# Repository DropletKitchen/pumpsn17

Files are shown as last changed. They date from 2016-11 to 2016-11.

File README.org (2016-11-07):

* Low-cost, High-performance Syringe Pumps for Microfluidics Applications

*This page describes how to build simple but high quality syringe pumps for microfluidics applications.*

This is a [[https://DropletKitchen.github.io][DropletKitchen]] project. Original source code of the project
is provided under MIT License. The source may contain code under a
different license, if this is the case it is stated in the LICENSE
file.

If not stated otherwise, the designs and documentation in this repository
is Copyright (c) 2016 Martin Fischlechner and DropletKitchen Contributors,
and made available under a
[[https://creativecommons.org/licenses/by/4.0/][Creative Commons Attribution 4.0 International (CC BY 4.0)]] License.

#+CAPTION: Image of the 3D-printed version of the pump.
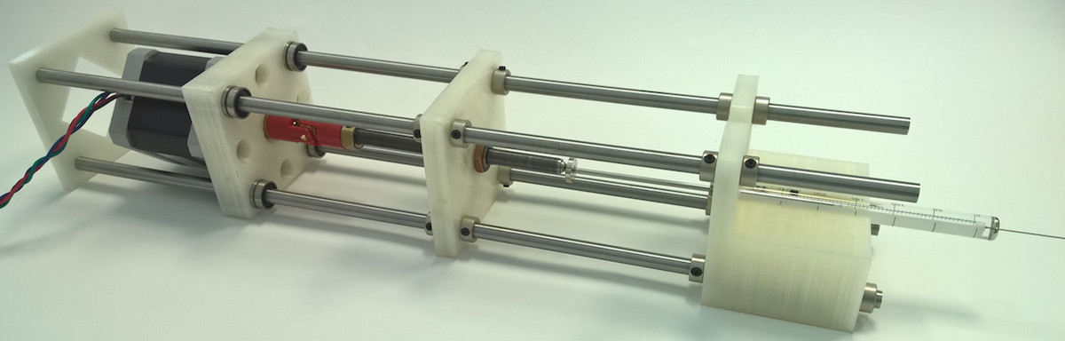
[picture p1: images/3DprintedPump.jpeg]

#+BEGIN_QUOTE
Image of the 3D-printed version of the pump.
#+END_QUOTE

** Introduction

These syringe pumps are infusion (push) only and have been designed to
be as simple as possible. We are using them for droplet microfluidics
and other microfluidics applications. They rival the performance of
commercial-grade, high-quality pumps and are suitable for professional
research.

To achieve constant flowrates without depending on an overly sturdy
structure, the leadscrew itself actuates the movement of the syringe
piston. This way, the pump only has to be rigid and aligned between
the parts holding the nut of the leadscrew and the syringe. Different
syringe diameters can be used by applying simple 3D-printed adaptors.
Screws and nuts for optics assemblies are employed, which, in
conjunction with microstepping the motor, result in stable flow even
at very low flowrates. The pump uses it's structural components as
endstops, and the user controls the system via a software frontend
based on Pure Data (Pd), a graphical programming language, which
allows for straightforward and live system automation, at a small
fraction of the cost of a commercial pump.

** Mechanics - Files and Bill of Materials   

*** Pump Design files (openSCAD)

To be able to adapt the design towards other hardware, we modelled it
in openSCAD (http://www.openscad.org/) in parametric form. Using the
Bill of Materials, BOM, below it should work out-of-the box, else you
will have to adapt the model. Please check dimensions first before
laser cutting/3D printing parts. In openSCAD, the variables are
defined in the header of the file, the rest of the code generating the
model then works with those values. This means it is very
straightforward to adapt the design towards your specific
requirements. In our experience, measuring sizes with a caliper and
directly putting these values into the model yields tight-fitting
parts once laser-cut. With a Fused Deposition Modelling, FDM,
3D-printer you should make some test prints first ('fit' depends on
material characteristics, print settings and the calibration of your
machine). Although you can make parts fit by filing and drilling, this
is cumbersome and should be avoided.

#+CAPTION: A screenshot of the pump in openSCAD (for the file see [[./files/SyringePump3Dmodel.scad]]).
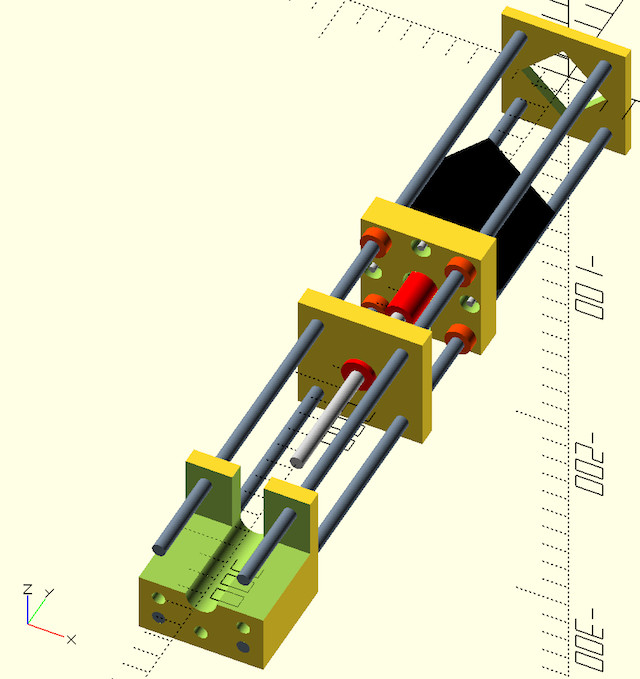
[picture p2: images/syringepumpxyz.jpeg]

#+BEGIN_QUOTE
A screenshot of the pump in openSCAD (for the file see
[[./files/SyringePump3Dmodel.scad]]).
#+END_QUOTE

#+CAPTION: Simple 3D-printed syringe adaptors to allow the use of syringes with different diameters (see [[./files/3DprintedSyringeAdaptors.scad]]). 
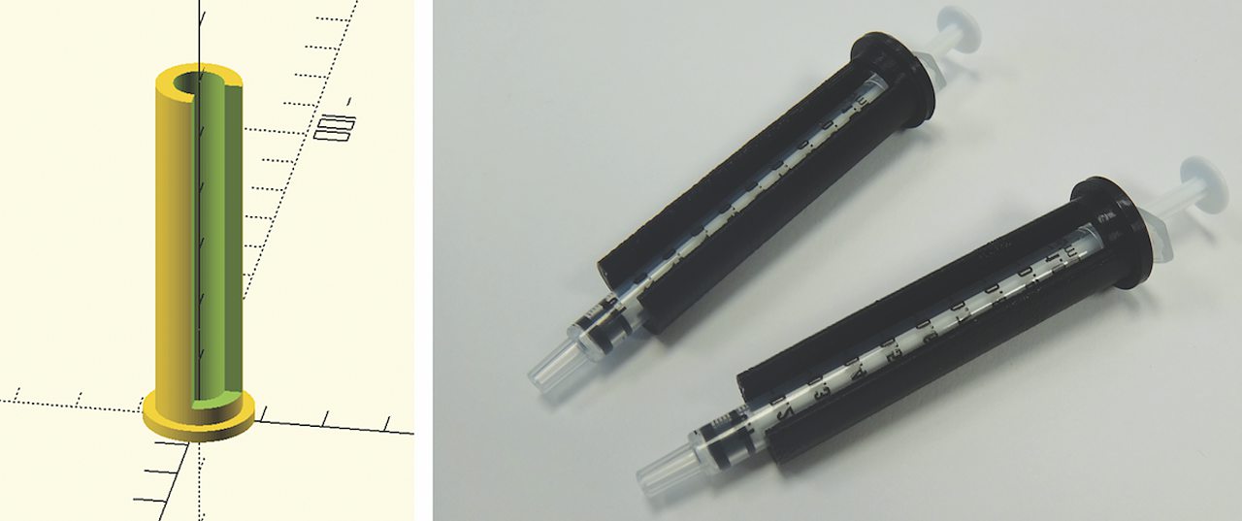
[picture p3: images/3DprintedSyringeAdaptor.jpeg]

#+BEGIN_QUOTE
Simple 3D-printed syringe adaptors to allow the use of syringes with
different diameters (see [[./files/3DprintedSyringeAdaptors.scad]]).
#+END_QUOTE

*** Bill of Materials

- this list is for a set of 4 syringe pumps, which should be
  sufficient to drive most microfluidic protocols. Cost of components
  is approximate.

| item [4X Syringe Pumps]                                        |      number | purpose               | bought from   |  part-no | approx  (£/euro) |
|----------------------------------------------------------------+-------------+-----------------------+---------------+----------+-------------|
| Allegro A4983 Based Stepper Boards: here the 'Big Easy Driver' |           4 | stepper board         | Technobots    | 2900-445 | ~ 70        |
| Nema 17 Steppers (400 steps/rev)                               |           4 | stepper motor         | Technobots    | 1402-050 | ~ 80        |
| Teensy 3.1 or 3.2 Microcontroller                              |           1 | control               | cpc-Farnell   |  SC13539 | ~ 20        |
| Fine Hex Adjuster, 1/4"-80, 4" Long                            |           4 | leadscrew             | Thorlabs      | F25SS400 | ~ 40        |
| Locking Phosphor-Bronze Bushing with Nut, 1/4"-80, L=0.50"     |           4 | leadscrewnut          | Thorlabs      |   N80L6P | ~ 28        |
| Silver Steel 6mm x 333mm                                       |          16 | pump structure        | Technobots    | 4426-006 | ~ 35        |
| Zinc Collets 6mm pk/4                                          |          24 | fasteners             | Technobots    | 4609-060 | ~ 28        |
| Linear Bearing LM6UU 6mm Bushing                               |          16 | slides motorpart      | Technobots    | 4604-606 | ~ 16        |
| Universal Coupling Body                                        |           4 | motor-screw-connector | Technobots    | 4604-050 | ~ 12        |
| Universal Coupling Insert - 5mm                                |           4 | motor-side            | Technobots    | 4604-059 | ~ 8         |
| Universal Coupling Insert - 1/4"                               |           4 | screw-side            | Technobots    | 4604-066 | ~ 8         |
| OTHER SMALL ITEMS                                              |             |                       |               |          |             |
| 95mm x 127mm Copper Clad Stripboard (or bigger)                |           1 | mount for electronics | Technobots    |          | ~ 2         |
| Male & Female PCB Headers 2.45mm pitch                         |        some | simple connectors     | cpc-Farnell   |          | ~ 10        |
| Sugru (good to isolate PCB-header-based connectors)            |             | or use hotglue-gun    | Maplins       |          | ~ 7         |
| Screws M3 (25mm): to mount motors                              |          16 |                       | Technobots    | 4300-006 | ~ 3 for 100 |
| Screws M3 (<10mm), optional                                    |        many | fix collets better    | Technobots    | 4300-002 | ~ 2 for 100 |
| Screws M6 (~100mm), syringe part lasercut version              |           8 | reduces acrylic       | hardware shop |          |             |
| USB (micro) cable                                              |           1 |                       | cpc-Farnell   |          | ~ 3         |
| 6 wire colored ribbon cable                                    |          4m |                       | Technobots    |          | ~ 3         |
| 12V/>=5A power supply                                          |           1 |                       | cpc-farnell   |          | ~ 20        |
| 3D-printer filament (PLA) or 5mm acrylic sheets(410X280)       | 1kg/5sheets | pump structure        | RS, Techsoft  |          | ~ 30        |
|----------------------------------------------------------------+-------------+-----------------------+---------------+----------+-------------|
|                                                                |             |                       |               | 4 pumps: | ~ 425       |

**** Companies:
- Technobots:  http://www.technobotsonline.com
- Thorlabs:    http:/www.thorlabs.com
- CPC-Farnell: http://cpc.farnell.com/
- RS:          http://uk.rs-online.com/web/
- Techsoft:    http://www.techsoft.co.uk/
- Maplin:      http://www.maplin.co.uk

All components but the optics-screws (Thorlabs) can be obtained
commercially. If other leadscrews are used, the software has to be
adapted to the distance/revolution grading.

**** Machines (and/or):
- Lasercutter (we used an Epilog, 30W): Often found in a local
  hackerspace or University Engineering Department. One could also use
  internet-based services.
- FDM 3D-printer (we use an Ultimaker 2 & PLA (natural white) material)

**** Tools:
- Soldering iron
- Hand tools (screwdrivers etc.)

** Mechanical Assembly of Pumps
*** Laser-cut version
- adapt the openSCAD model to your needs by changing the variables as
  you see fit and rendering the model.

- export .stl-files of all the parts (syringe-part, leadscrew-part,
  motor-part, end-part). It is easiest to comment-out all parts but
  one, render and export to .stl.

- import the .stl files into openSCAD, orient them so that the
  projection you want is at (0,0,0). Render and export as .dxf-file,
  which can then be directly used by a laser cutter.

  #+BEGIN_SRC C :exports code      
  projection(cut=true) 
  translate ([0, 0, 0]) 
  rotate ([0,0,0])
  import("/pathtofile/file.stl"); 
  // comment projection out first, adjust translate/rotate (slices at 0,0,0),
  // uncomment projection(cut=true),render, export to .dxf
  #+END_SRC

- cut out all the parts. It might be a good idea to check dimensions
  and fit first by cutting a trial sample.

- if you use the components from above, you should be able to use the
  .dxf-file provided ([[./files/PumpPartsLaserCut.dxf]]; see
  below). To work with 2D-CAD files we use the free version of
  Draftsight
  (http://www.3ds.com/products-services/draftsight-cad-software/free-download/).

#+CAPTION: Left: Laser cut parts for one pump. Right: Image of components.
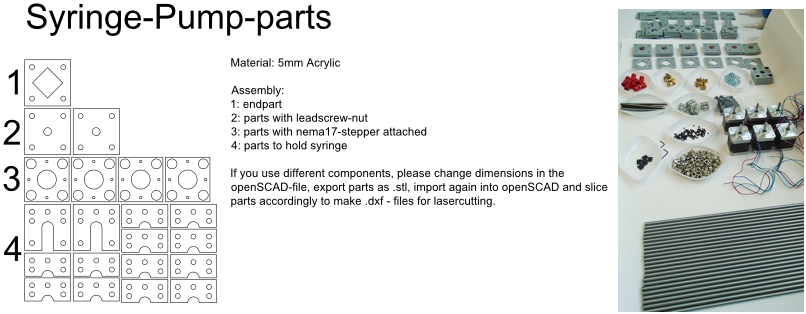
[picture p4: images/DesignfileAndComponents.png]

#+BEGIN_QUOTE
Left: Laser cut parts for one pump. Right: Image of components.
#+END_QUOTE

**** Pre-Assembly of Parts
***** Motor Part
- tin the leads of the motors with solder, add a male
  PCB-connector (or any other connector of your choosing. On our
  motors the colored leads are GREEN, BLACK, BLUE, RED).
- we use Sugru to electrically isolate the connectors at the end.
- add the connector for the leadscrew (5mm brass insert) to the
  motor - you might not have space to do that later.
- depending which length of M3 screws you have used to mount the motor, you
  will need different quantities of acrylic sheets. LM6UU bearings are
  19mm in length, so 4X5mm sheets are fine. If you have longer screws,
  either add nuts or fit in some more acrylic sheets.
- slot the 4 bearings into the stack of parts (should be lightly
  press-fit); screw the assembly together. The bearings do not have to
  bear much load. If they aren't fixed well enough use a dab of epoxy glue.

***** Leadscrew Part
- take the two acrylic sheets and mount the leadscrew-nut.
- add the brass insert to connect the motor onto the leadscrew
- insert the screw VERY carefully to avoid damaging the thread which can
  happen rather easily.

#+CAPTION: Pre-assemble motor with leadscrew (bottom right) and component inventory.
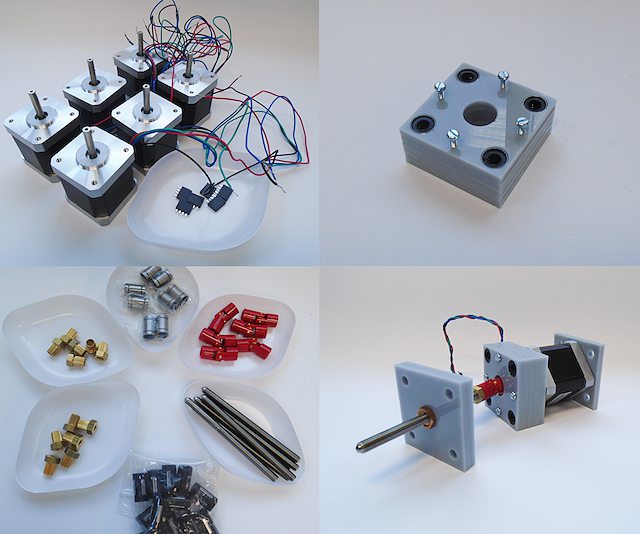
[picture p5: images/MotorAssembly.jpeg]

#+BEGIN_QUOTE
Pre-assemble motor with leadscrew (bottom right) and component inventory.
#+END_QUOTE

***** Syringe Part
For this part one should design towards specific needs. 
Make sure the cutouts are big enough for your syringes. If you want to
use different syringes with different diameters, adjust the
CAD-model to the thickest diameter and 3D-print/laser cut adaptors that
can be quickly exchanged.The adaptors must allow the piston of
the syringe to reside exactly in the centerline of the screw.

You can either cut many slides and assemble as a stack, or use some
long M6 screws and attach pairs of parts with M6 nuts. If you use tape
to hold the syringes in place (which works fine), filling the
structure with acrylic plates provides a continuous surface for fixing
the tape in place.

**** Assembly of the Pump
- take 4 of the 6mm steel shafts, round off the edges with a file to
  ease assembly.

- slot the steel shafts into the assembled motor part. Take care not
  to harm the LM6UU linear bearings. 

- add endpart, leadscrew-part and syringe part. Do not forget to
  insert the collets (8 collets/part, before and after). Don't fix
  them yet.

- measure the length of the syringes you want to use. There is no
  electronic endstops put into the design to keep assembly-time to a
  minimum (although it could be done rather easily). To make sure that
  your (glass) syringes stay unharmed, the length between the syringe-
  and the leadscrew part should be adjusted such that the movement
  will be blocked mechanically before crushing the syringe. The
  endpart should be mounted such that the movement will be blocked
  before the leadscrew turns itself out of its nut. If the motor hits
  these points it will stall, making a different noise than usual, but
  else stay unharmed. Don't forget to adjust the power of the motor on
  the respective potentiometer on the stepper driver board. With
  maximal power applied, the stepper motor can damage the assembly.

#+CAPTION: Three pumps before adjusting the leadscrew part & fixing everything with collets.
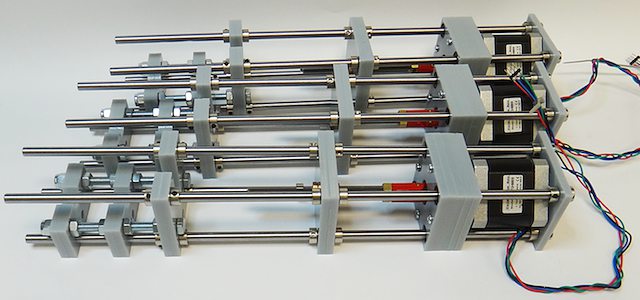
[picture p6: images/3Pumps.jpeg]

#+BEGIN_QUOTE
Three pumps before adjusting the leadscrew part & fixing everything
with collets.
#+END_QUOTE

- fix the collets of the syringe part. In general it is a good idea to
  use short M3-screws instead of the small hex-screws provided for
  making repeated opening/closing easier.

- add the electronics to the motor and drive it back and forth (at
  this point you could add some lithium grease or other lubricant).
  The leadscrew-part has to be adjusted such that the turning
  leadscrew stays centered without wobble. Use your syringes to adjust
  the length between leadscrew and syringe part. This serves as a
  mechanical endstop for forward movement. Handle the position of the
  endpart accordingly to stop backward motion. Then fix the collets
  securely.

- when finished use a bit of epoxy glue to permanently connect the
  'universal coupling body' with the brass inserts. The assembly can
  still be taken apart by loosening the grub-screws holding the motor
  shaft and the leadscrew together.
 
- done!     

*** 3D-Printed Version
Depending on the calibration of your FDM-printer, parts might need
some 'adjustments'. Please print calibration pieces first to make sure
the parts are well fitting. If needed, you can use a drill-bit or a
round file to make adjustments but it is not much fun. Assembly of
pumps is similar to the lasercut version. To generate the .stl-files
for printing, it is easiest to comment out all parts but one in the
openSCAD model, render and export.

#+CAPTION: Two modified 3D-printed pumps with smaller, lower power Nema14 motors used in a microfluidic experiment. The electronics in the image is based on a 'Quadstepper board' (unfortunately no longer available). 
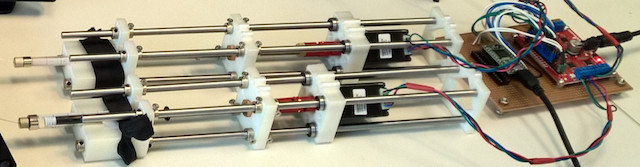
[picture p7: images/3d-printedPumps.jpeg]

#+BEGIN_QUOTE
Two modified 3D-printed pumps with smaller, lower power Nema14 motors
used in a microfluidic experiment. The electronics in the image is
based on a 'Quadstepper board' (unfortunately no longer available).
#+END_QUOTE

** Electronics
To drive the stepper motors of the pumps we use a A4983 stepper driver
chip from Allegro Microsystems (datasheet
http://www.technobotsonline.com/Datasheets2/1518-009-A4983SETTR-T.pdf).
For convenience we use one 'Big Easy Driver' for each motor
(http://www.technobotsonline.com/big-easy-driver.html,
http://www.schmalzhaus.com/BigEasyDriver/). The 'Big Easy Driver'
boards are nice, because they default to 16 step microstepping mode,
when the 'MS1, MS2, MS3' pins are left unconnected (which means that
less soldering has to be done). With 16-step microstepping, one
revelation of the leadscrew (318 micrometer movement) is divided into
400*16=6400 steps resulting in a stable flow even at very low
flowrates. If you use a stepper with 200 steps/revolution (1.8 instead
of 0.9 degrees/step), the pumps will still work very well but you will
have to adjust the calibration in the software. If you are prepared
for some more soldering, any stepper driver board used in common FDM
3D-printers should do just fine. The stepper drivers are controlled
with a teensy 3.1 or 3.2 microcontroller. The teensy has 3.3V logic
levels, so put a solder-blob onto the stepper drivers to switch them
from 5V (default) to 3V logic.

#+CAPTION: Left: Images of the electronics board with three stepper driver boards mounted. Right: Schematic diagram.
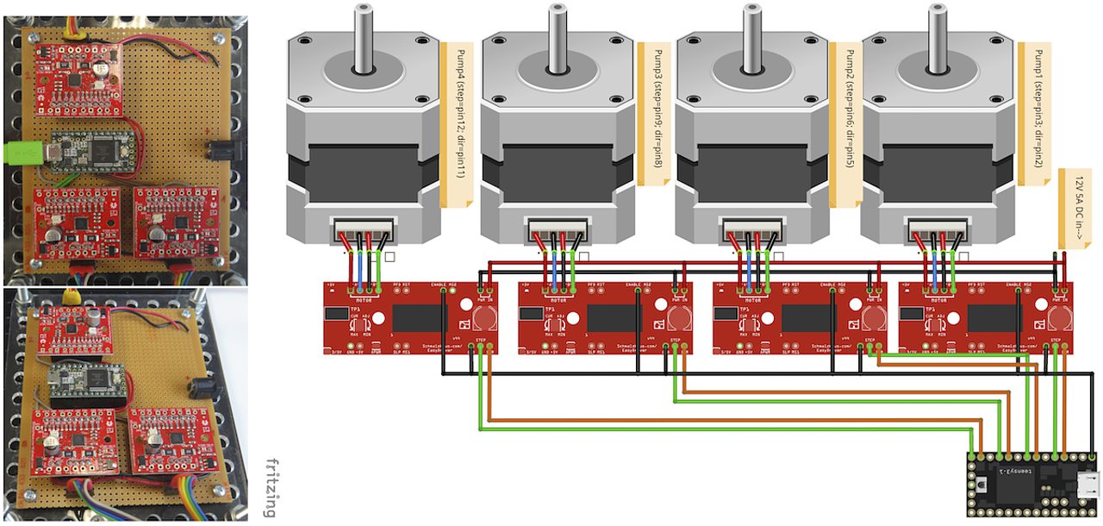
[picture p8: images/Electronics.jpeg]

#+BEGIN_QUOTE
Left: Images of the electronics board with three stepper driver boards
mounted. Right: Schematic diagram.
#+END_QUOTE

*** Make the board
- solder connectors onto the driver board (e.g. PCB-connectors)

- layout the parts on a stripboard and drill holes so that you can
  mount the board with screws to an enclosure (e.g. from laser-cut
  acrylic).

- solder female PCB-connectors on the board for the teensy and the
  stepper boards (don't forget to cut the traces on the stripboard
  underneath).
- make all the necessary connections (see layout...)

- we made the system as simple as possible: 
  - no connection to MS1, MS2, MS3 - all are pulled high when not
    connected (means the driver defaults to 16 microstep-mode
  - no connection to sleep (slp) and reset (rst) - if powered the
    system will be on all the time. If you want to shut down the
    motors, turn off the power.
 
  - this leaves only the following connections to be made:
    - enable (en) is pulled low on all by connecting to ground (this
      is important, else the pins float).
    - shared GND between teensy and the quadstepper board (or single
      big easy drivers)
    - step-pin (stp): if high for >1 microsecond, the motor will step
    - direction-pin (dir): high/low sets the direction (if your pump
      steps the 'wrong' direction, just reverse the connections of the
      leads from (e.g. green, black, blue, red --> to red, blue,
      black, green).

  - Teensy is powered by a USB connection and the motors are powered
    separately (we use a 12V 5A power supply).

- Don't forget to adjust the current supplied to the motor with the
  small potentiometer on the stepper driver board. On max, the chip
  gets hot and the motor might have enough torque to continue beyond
  the end-stop, damaging the pump assembly.

* Software for Syringe Pumps
** Introduction - mode of operation and choice of tools

The pumps are controlled with a microcontroller (a 'teensy' 3.2 or
3.1) and a software front end written in Pure Data (PD). The teensy
(https://www.pjrc.com/teensy/teensy31.html) is a 3.3V, 32-bit ARM
based microcontroller that is compatible with the Arduino toolchain
(https://www.arduino.cc/en/Guide/HomePage) and therefore easy to
program. The prime reason to use a teensy is the high speed USB data
transfer they allow
(https://www.pjrc.com/teensy/benchmark_usb_serial_receive.html). Apart
from controlling machinery, the teensy is well suited for data
acquisition tasks.

Pure Data (PD, https://puredata.info/) is an open source dataflow
programming language used primarily for music and video applications.
It runs on nearly every computing platform, is straightforward to
learn and can be modified 'live', which is great for microfluidics
experimentation.

The communication protocol between the microcontroller and PD is OSC
('Open Sound Control', https://www.opensoundcontrol.org). It is a very
flexible, easy to use two-way communication.

#+CAPTION: System diagram.

#+BEGIN_QUOTE
System diagram.
#+END_QUOTE

** Install the Software Toolchain
*** Arduino/Teensyduino
The easiest way to program teensy microcontrollers is to use the
Arduino IDE (download:https://www.arduino.cc/en/Main/Software). For
the teensy microcontrollers to be recognised by the Arduino IDE, one
must additionally install 'Teensyduino' (download:
https://www.pjrc.com/teensy/td_download.html). There is a detailed
tutorial on software installation and its use on the webpage. Most of
the Arduino libraries are compatible with teensy, Teensyduino itself
comes with many optimized ones (full install recommended).

*** Install Pure Data (PD) 
Pure Data can be downloaded from the PD community site
(https://puredata.info/downloads) and installation is straightforward.

For Mac or Win you should choose to install PD-extended, which is
pre-packaged with many additional externals from the community (all
necessary things needed for this project should be installed per
default). PD-extended is not actively maintained any more, but still
works well. Alternatively you can use PD-Vanilla and install externals
via the 'deken'-plugin (https://github.com/pure-data/deken) as
required.

On a Linux system, you should use 'PD-L2ORK'
(http://l2ork.music.vt.edu/main/make-your-own-l2ork/software/), an
up-to-date, maintained and beautified version of PD-extended from the
'Linux Laptop Orchestra' (Virginia Tech Music Department). Beta
versions for Mac and Win are now also available. PD-L2ORK runs well on
Ubuntu, but also under Raspbian on Raspberry Pi Model 2 and 3. This
allows a small touchscreen interface to be used resulting in a
small-footprint solution.

#+CAPTION: Raspberry Pi Model 3 based  to control syringe pumps. The files for the lasercut enclosure are based on a design by Sparkovsky on Thingiverse (https://www.thingiverse.com/thing:1441432).
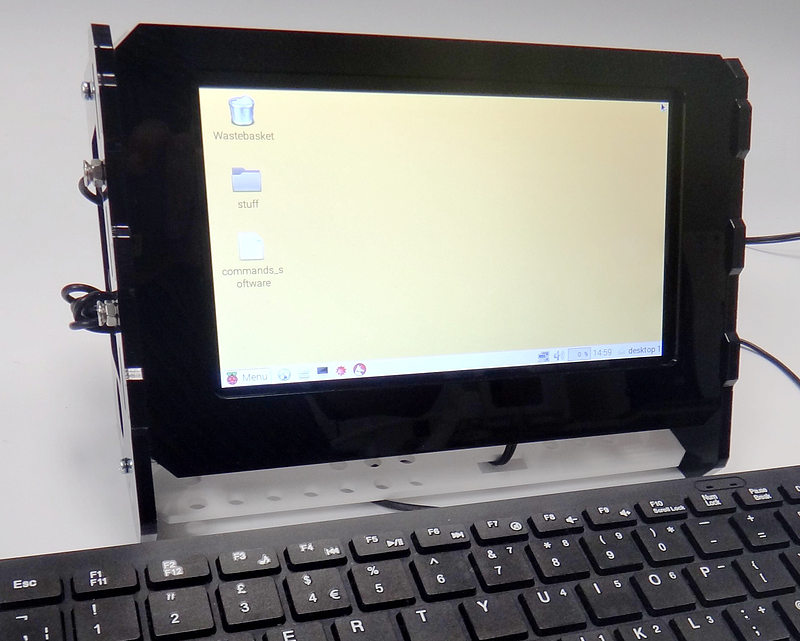
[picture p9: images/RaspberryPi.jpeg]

#+BEGIN_QUOTE
Raspberry Pi Model 3 used to control syringe pumps. The files for the
lasercut enclosure are based on a design by Sparkovsky on Thingiverse
(https://www.thingiverse.com/thing:1441432).
#+END_QUOTE

** Setting up the System 
- program the teensy
- open the PD-program 
     - and you should (almost) be ready to go. 

You can test the system without the microcontroller attached to the
pumps. If the communication works via OSC, the flow rates you transfer
(in microL/h) and the direction of movement will be mirrored in the
smaller sliders beneath the main control elements in the PD-frontend.

** How the System Works  
In a nutshell, the desired flowrate (in uL/h) is converted into a
delay time (in microseconds) which defines when the motor on the pump
has to step. To make this delay time as precise as possible, an
interrupt routine is used that checks every 10 microseconds if a motor
has to be stepped or not - no matter what the rest of the program is
doing at that time. Flow rate to delay time conversion is dependent on
the type of motor (steps/rev), thread-type of the leadscrew used
(microns/revolution) and syringe diameter.

We supply two versions of the programs here that differ where these
calculations take place:
 
- 'Hardcoded': directly on the microcontroller (PD transfers the flow
  rate value, the syringe diameter and other values are to be changed
  in the program running on the teensy). This is convenient if one
  always works with syringes of a certain diameter.
- 'Flexible': all calculations are done in PD and the resulting delay
  times in microseconds are transferred. This allows all parameters in
  PD to be changed on the fly without reprogramming the
  microcontroller when changing hardware.

** Getting it to Run
*** 'Hardcoded' Version (calculations on the teensy)
- upload the corresponding file to the microcontroller
  ([[./files/Hardcoded4Pumps.ino]]). Have a look at the code, everything
  you can and might have to change should be explained in the
  comments.
- place the PD-program ([[./files/Hardcoded4Pumps.pd]]) together with a
  little helper-program for OSC ([[./files/o.io.slipserial.pd]]) in a
  folder and open it in PD-extended or PD-L2ORK.

#+CAPTION: Screenshot of the program. 
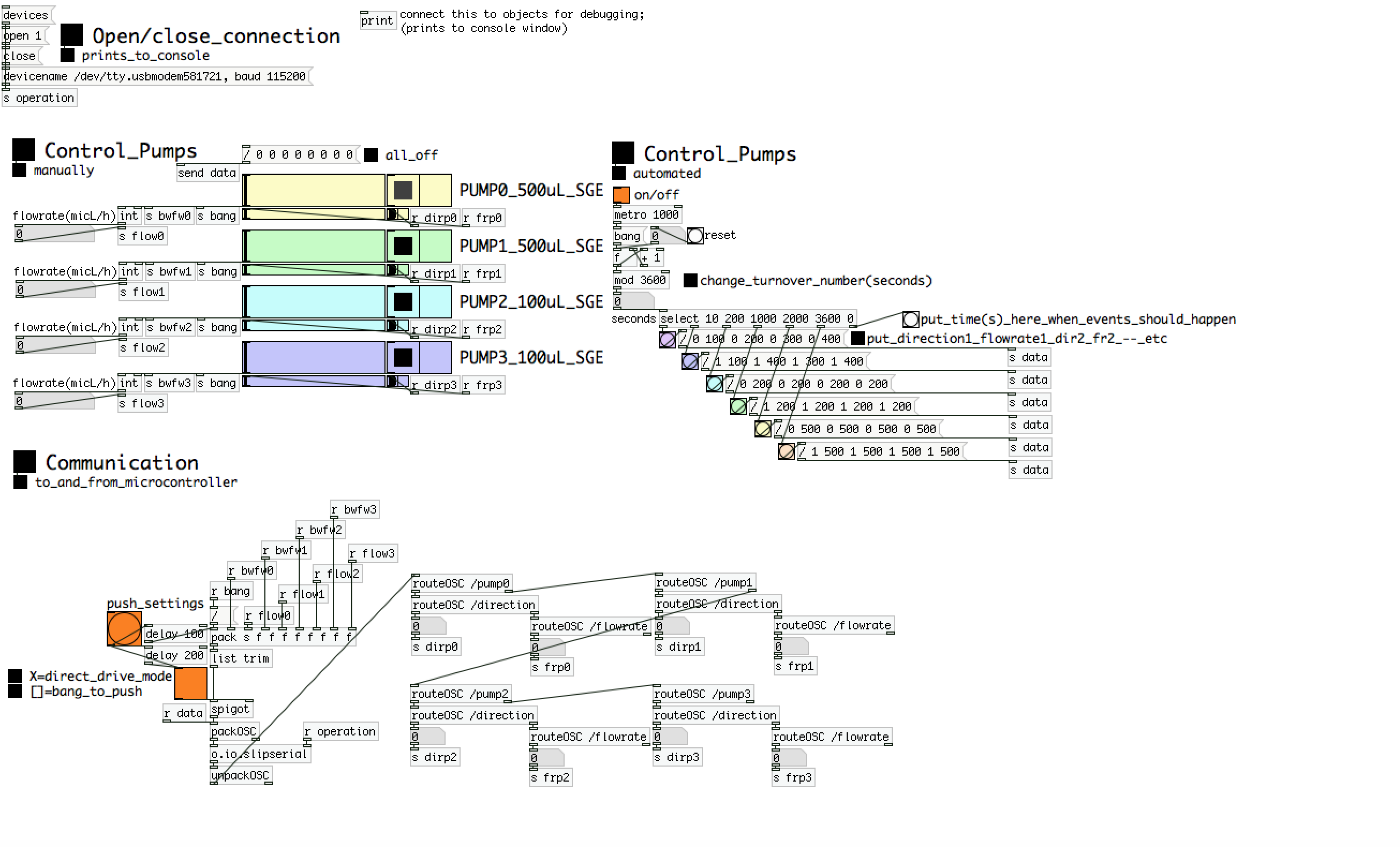
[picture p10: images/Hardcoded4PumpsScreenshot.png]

#+BEGIN_QUOTE
Screenshot of the program. 
#+END_QUOTE

- Hit [devices], and the available serial ports will show in the
  console window. One of them is connected to the teensy. Click [open
  x[ (change the numbers by entering editing mode, ctrl-e (linux),
  cmd-e (mac)) and PD should connect to the teensy.

- The section 'Control Pumps Manually' allows you to dial in your
  desired flow rate for each pump. The buttons on the right side of
  the sliders will change direction. If you right-click on an item/box
  a properties and help dialog is available which lets you learn and
  customize. If the values are transferred to the teensy, the
  microcontroller will send the list of numbers back. Those are
  displayed underneath and give immediate visual feedback. If you have
  the pumps connected and powered, you should see the changes there
  too.

- To transfer the pump settings, you have to click the orange 'bang'
  in 'Communication to and from microcontroller'. For immediate
  response when changing settings, click the orange toggle switch to
  mark it [X].

- 'Control Pumps Automated' is a simple tool for automation. Setting
  the toggle-switch to 'on' [X] activates a counter (per default here
  in seconds) which will turnover to 0 after some time (here 1h). The
  [select] box activates the attached lists of numbers (direction
  pump1 flowrate pump1 ....) after the dialled-in times. To change it,
  get into edit-mode, change the values and the numbers of events to
  your liking (you will have to copy/paste/delete structures and
  reconnect).

*** 'Flexible' Version (calculations in PD) 
This version of the programme is reduced in its footprint to be
displayed on a 7" screen (in our case a raspberry Pi Model 3 with a
touchscreen). It uses PD's 'Graph on Parent (GOP)' feature which
allows program complexity to be hidden. It is used similarly as above,
but lets you select serial ports as well as syringe diameters. The
right-hand part outside the 'GOP' can be modified for more complex
automation.

#+CAPTION: Screenshot of the program. 
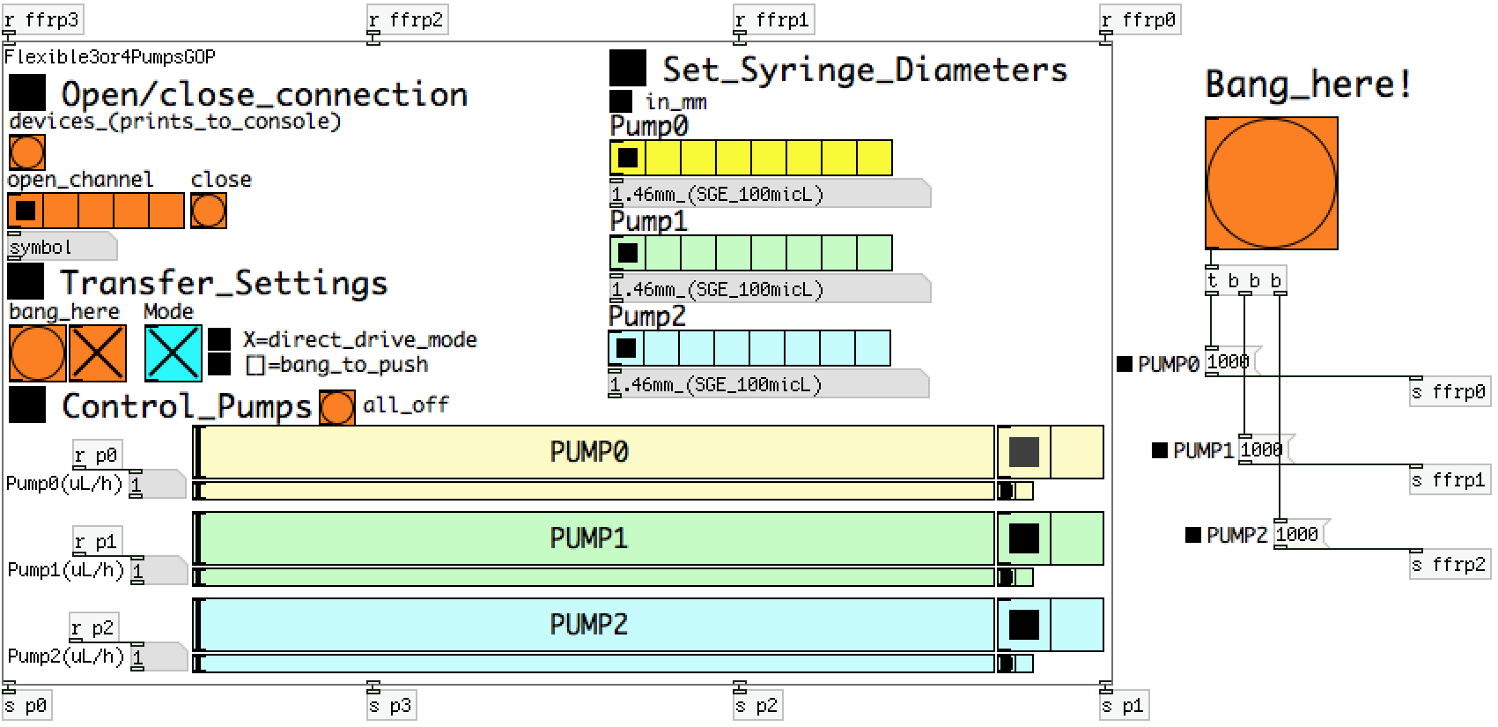
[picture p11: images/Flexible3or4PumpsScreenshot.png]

#+BEGIN_QUOTE
Screenshot of the program.
#+END_QUOTE

- upload the corresponding file to the microcontroller
  ([[./files/Flexible3or4Pumps.ino]]).
- place the PD-programs ([[./files/Flexible3or4Pumps.pd]]) and
  ([[./files/Flexible3or4PumpsGOP.pd]]) together with a little
  helper-program for OSC ([[./files/o.io.slipserial.pd]]) in a folder and
  open it in PD-extended or PD-L2ORK.
- The file 'Flexible3or4Pumps.pd' is the software front end. If you
  want to change the program in any way, changes have to be conducted
  in 'Flexible3or4PumpsGOP.pd'. The program actually contains controls
  for 4 pumps, but only 3 are shown in the front end. To have a 4-pump
  system, enlarge the red 'GOP' rectangle and move the controls for
  the 4th pump into the space. It will then show in the front end. The
  calculations in 'Flexible3or4PumpsGOP.pd' should be simple to adapt
  to modified hardware.

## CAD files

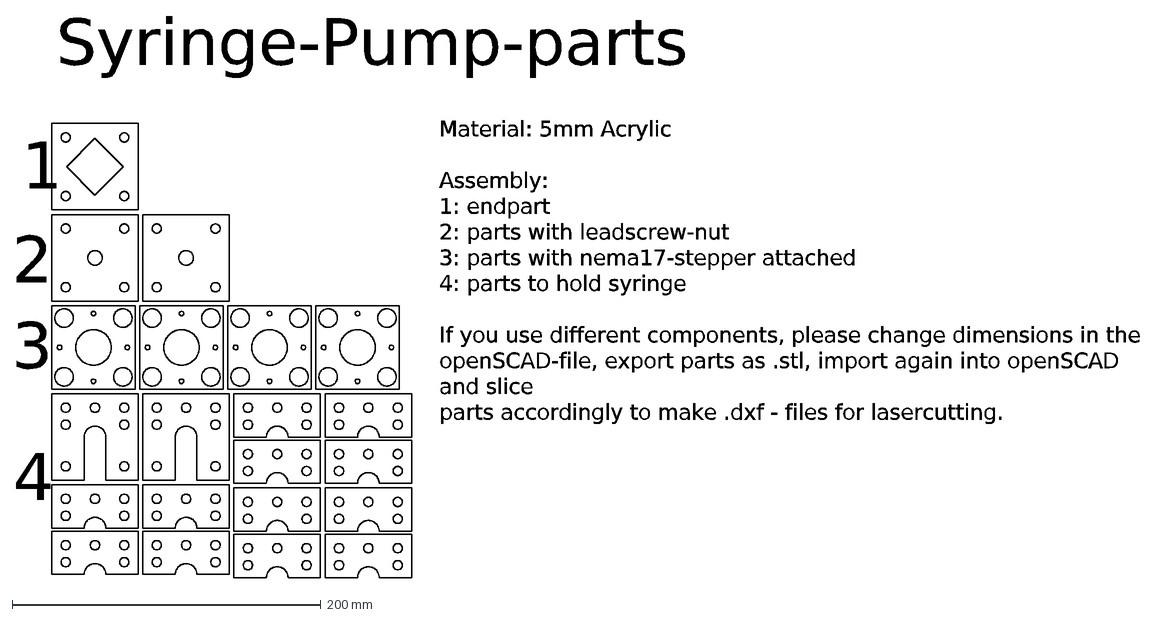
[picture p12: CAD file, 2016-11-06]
files/PumpPartsLaserCut.dxf
Syringe-Pump-parts
Material: 5mm Acrylic Assembly: 1: endpart 2: parts with leadscrew-nut 3: parts with nema17-stepper attached 4: parts to hold syringe If you use different compo
2
1
3
4

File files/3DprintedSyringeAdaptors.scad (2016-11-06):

//syringe adaptors for pumps with a 14mm diameter cut-out
// r of our syringes are:
//Hamilton 200uL/500uL: OD 7.75; (r=3.875)
//1mL plastic: OD 7mm
//ring for 5mL BD: 14.75mm (fits into default part but neets 5mm ring)
//sge glass 100 & 250micL r=4.5+0.25
//default length of connector: 60mm

//variables
length_syringe=60; //put in desired length of the part (might depend on syringe)
syringe_r=4.5 +0.25; //radius of the syringe in question + material/3D-printer dependent addition for easy fit (here 0.5mm), 

cutout_r=7; //radius of the cut-out in the 'syringe-part' of the pump = outer cylinder of part, here 7

fix_r=cutout_r+2; //feature to fix connector (add 2mm)
fix_h=2;

rim=10; //length of plastic all around
//model

difference ()
{
    translate ([0,0,0]) 
    rotate ([0,0,0])
    union ()
        {
            cylinder(r = cutout_r, h = length_syringe, $fa=1, $fs=0.5);
            cylinder(r = fix_r, h = fix_h, $fa=1, $fs=0.5);
        }
        
    cylinder(r = syringe_r, h = 4*length_syringe, $fa=1, $fs=0.5, center=true);
    translate ([0,0,rim/2])    
    cube ([2*syringe_r, 2*syringe_r, length_syringe]);
}

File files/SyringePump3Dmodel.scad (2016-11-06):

///////////////////////////////////////////////////////
/////////////Simple Syringe Pump//////////////////////
//////////////////////////////////////////////////////


//////////////////This version is for a///////////////
/////////////Stepper Motor NEMA 17, 42x48mm, /////////


//////////////////////////////////////////////////
//variables:
// change these according to the parts you use
/////////////////////////////////////////////////

width = 54; //x overall, minimum = diagonal height of motor; check if motor fits into steelbars, often edges are rounded of, so you can be a little smaller
depth = 54; //y overall, minimum = diagonal height of motor
min_wallsize = 2; //minimum wallsize of parts
shaft_r = 3; //radius of shafts, in endpart, leadscrewpart, syringepart 
diameter_steelbar=2*shaft_r;
slip = 2; //'biggerness' of all other parts for movement of motor part, 2 means 1mm smaller on every side

//endstops: commented out here, remove '*' if you want to use endstops
endstopholes_r = 3; //radius of screws/shaft used for endstops
endstopholedistance = 20; //don't forget space for collets/nuts, >4*endstopholes_r
 

//specific variables syringepart
height_syringepart = 50; //z-height of part
syringe_r = 7; //syringe diameter of a 5mL syringe (the biggest we would ever use)

//specific variables leadscrew part
height_leadscrewpart = 9; //z-height of part, must fit to thread of leadscrewnut (max 10mm with our nuts)
nut_r = 4.75; // (dia=9.5mm) leadscrew-nut thread


//specific variables motor part
height_motorpart = 14; //z-height of part (should be corresponding to length of bearings LM6uu=18.8mm, or, as here, the length of motor screws available (-3mm to hold motor in firmly) 
bearing_r = 6; //radius of bearing, LM6UU=12mm dia
motor_r = 8; //radius of middle 'hole' of motor, big enough for screw-motor-connector
motor_r2 = 11.5; //radius of middle 'round' of motor, dia=15mm +1 extra, only more stylish, not really necessary (eg for slicing the part for lasercutting)

motor_screw_r = 1.5; //radius of screws that hold stepper in, 3mm diameter (M3)
motorscrew_length = 8; //effective length of screw to mount motor (length - 3mm to hold motor)
motor_screw_hole_r = 4.5; //radius of hole to mount screws (that are not long enough), not necessary if you have long enough screws
motor_screw_distance = 31; //distance between motor_screws

//specific variables endpart
height_endpart = 5; //z-height of part

//variables to arrange parts for visualization and for put-in hardware components 
shaft_length = 333;//total length of steelshafts
motor_length = 48;
motor_width = 42; 
motor_halfdiagonal = 0.5* sqrt(2*(motor_width*motor_width)); //half the diagonal of square area of motor, could be too big when edges of motor are rounded
insert_radius=sqrt(2*(diameter_steelbar*diameter_steelbar));
place_motorpart = 120;//place where motorpart is put
place_leadscrewpart = 180;//place where leadscrewpart is put

shaftcoupler_length = 34;
shaftcoupler_radius = 6.5;

length_bearing = 19;

leadscrew_length = 101;
leadscrew_radius = 3.05;
leadscrewnut_totallength = 13.5;
leadscrewnut_maxradius = 7.5;



echo ((width/2 - (bearing_r + min_wallsize)));

rotate([90, 0, 0]) { //rotates the full model, comment out when you want to draw things, makes it easier, don't forget to comment out the '}' at the very end

/////////////////////////////////////////////////////////////
/////////////////syringepart////////////////////////////////
////////////////////////////////////////////////////////////

translate ([0, 0, (shaft_length-height_syringepart)]) //put part Zmm above 0,0,0
difference ()
{
translate ([0, 0, height_syringepart/2]) 
cube ([width + slip, depth + slip, height_syringepart], center = true);

//half-part carrying syringe
translate ([0, 0.5*depth, 0.65*height_syringepart]) 
cube ([1.1*width, depth, height_syringepart], center = true);
//syringe acess opening
translate ([0, 0.5*depth, 0.25*height_syringepart]) 
cube ([2*syringe_r, depth, height_syringepart], center = true);

//center square-hole where syringe fits in
translate ([0, 0, -(0.1*height_syringepart)]) 
cylinder(r = syringe_r, h = 1.2*height_syringepart, $fa=1, $fs=0.5);

//shaft-holes
//right top
translate ([(width/2 - (bearing_r + min_wallsize)), (depth/2 - (bearing_r + min_wallsize)), -(height_syringepart) ]) 
cylinder(r = shaft_r, h = 3*height_syringepart, $fa=1, $fs=0.5);
//right bottom
translate ([(width/2 - (bearing_r + min_wallsize)), (-(depth/2 - (bearing_r + min_wallsize))), -(height_syringepart) ]) 
cylinder(r = shaft_r, h = 3*height_syringepart, $fa=1, $fs=0.5);
//left top
translate ([(-(width/2 - (bearing_r + min_wallsize))), (depth/2 - (bearing_r + min_wallsize)), -(height_syringepart) ]) 
cylinder(r = shaft_r, h = 3*height_syringepart, $fa=1, $fs=0.5);
//left bottom
translate ([(-(width/2 - (bearing_r + min_wallsize))), (-(depth/2 - (bearing_r + min_wallsize))), -(height_syringepart) ]) 
cylinder(r = shaft_r, h = 3*height_syringepart, $fa=1, $fs=0.5);

//additional holes to mount 'things' with screws if needed

//left middle
translate ([(-(width/2 - (bearing_r + min_wallsize))), (-(bearing_r + min_wallsize)), -(height_syringepart) ]) 
cylinder(r = shaft_r, h = 3*height_syringepart, $fa=1, $fs=0.5);
//right middle
translate ([(width/2 - (bearing_r + min_wallsize)), (-(bearing_r + min_wallsize)), -(height_syringepart) ]) 
cylinder(r = shaft_r, h = 3*height_syringepart, $fa=1, $fs=0.5);
//middle bottom
translate ([(0), (-(depth/2 - (bearing_r + min_wallsize))), -(height_syringepart) ]) 
cylinder(r = shaft_r, h = 3*height_syringepart, $fa=1, $fs=0.5);
}

////////////////////////////////////////////////////////////
/////////////leadscrewpart////////////////////////////////////
//////////////////////////////////////////////////////////

translate ([0, 0, place_leadscrewpart]) 

difference ()
{
union ()
{
translate ([0, 0, height_leadscrewpart/2]) 
cube ([width + slip, depth + slip, height_leadscrewpart], center = true);

//add endstop-structure
translate ([-endstopholedistance/2, depth/2+endstopholes_r, 0])
*cylinder(r = 2.5*endstopholes_r, h = height_leadscrewpart, $fa=1, $fs=0.5); 
translate ([endstopholedistance/2, depth/2+endstopholes_r, 0])
*cylinder(r = 2.5*endstopholes_r, h = height_leadscrewpart, $fa=1, $fs=0.5);   
}

//endstop holes
translate ([-endstopholedistance/2, depth/2+endstopholes_r, -height_leadscrewpart])
*#cylinder(r = endstopholes_r, h = 3*height_leadscrewpart, $fa=1, $fs=0.5); 
translate ([endstopholedistance/2, depth/2+endstopholes_r, -height_leadscrewpart])
*#cylinder(r = endstopholes_r, h = 3*height_leadscrewpart, $fa=1, $fs=0.5);

//center square-hole where leadscrewnut fits in
translate ([0, 0, -(0.1*height_leadscrewpart)])
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

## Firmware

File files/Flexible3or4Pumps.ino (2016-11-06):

    ////////////////////////////////////////////////////////////////////
    ///////////////////Syringepump controller///////////////////////////
    ////////for teensy 3.1 or 3.2, and stepper drivers based//////////// 
    //and a OSC (open sound control) based frontend in pure data (PD)///
    ////////////////////////////////////////////////////////////////////

    // This version is 'flexible' - all variables (syr. diameter, motor, leadscrew, microstepping etc.)
    // are defined in the PD-frontend
    
    /*
    Electronics:
    -stepper boards are based on the Allegro A4988 stepper driver chip
    
    -enable must be low (ground)
    -MS1, MS2, MS3..if not connected they are pulled high (means it defaults to sixteenth step microstepping) 
    -GND together with teensy
    -step high/low ... minimum 1 microsecond required
    
    -WIRING:
    TEENSY pin
    
    pump0
    PIN 2 DIR
    PIN 3 STEP
    
    pump1
    PIN5 DIR
    PIN6 STEP
    
    pump2
    PIN8 DIR
    PIN9 STEP
    
    pump3
    PIN11 DIR  
    PIN12 STEP   


    How it works:
    The delaytime (delayUS) in microseconds ('inValue') and the direction (clockwise/counterclockwise, 'inDirection') 
    for all four pumps is transferred from the PD-frontend to the microcontroller via the OSC (Open Sound Control) protocol.
    If the microcontroller received a set of values it will send them back to PD, where it is used to 
    confirm that the communication works.

    The delaytime (specific to a given flowrate and the other parameters (syringe diameter, motors, microsteps, leadscrew)) 
    defines when a step has to be performed and is calculated entirely in the PD-frontend.

    If a step is due is determined by jumping into an interrupt every 10 microseconds. 
    If so, the step-pin is pulled high for 1 microsecond, then pulled low again.

    
    -This program is licensed under The MIT License (https://opensource.org/licenses/MIT), Copyright (c) 2016, Martin Fischlechner,
    with the exception of the code-blocks for initializing, receiving and sending OSC-messages, which were copied from https://github.com/CNMAT/OSC/tree/master/examples
    and have the following, similarly liberal, license: [the code-blocks are marked //&&; //&&] 
    
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
    IN NO EVENT SHALL REGENTS BE LIABLE TO ANY PARTY FOR DIRECT, INDIRECT,
    SPECIAL, INCIDENTAL, OR CONSEQUENTIAL DAMAGES, INCLUDING LOST PROFITS, ARISING
    OUT OF THE USE OF THIS SOFTWARE AND ITS DOCUMENTATION, EVEN IF REGENTS HAS
    BEEN ADVISED OF THE POSSIBILITY OF SUCH DAMAGE.

    REGENTS SPECIFICALLY DISCLAIMS ANY WARRANTIES, INCLUDING, BUT NOT LIMITED TO,
    THE IMPLIED WARRANTIES OF MERCHANTABILITY AND FITNESS FOR A PARTICULAR
    PURPOSE. THE SOFTWARE AND ACCOMPANYING DOCUMENTATION, IF ANY, PROVIDED
    HEREUNDER IS PROVIDED "AS IS". REGENTS HAS NO OBLIGATION TO PROVIDE
    MAINTENANCE, SUPPORT, UPDATES, ENHANCEMENTS, OR MODIFICATIONS. 
    */
    
    //library for interrupt
    #include <TimerOne.h>
    ///libraries and code for OSC communication
    #include <OSCBundle.h>
    #include <OSCBoards.h>

    //&&
    #ifdef BOARD_HAS_USB_SERIAL
    #include <SLIPEncodedUSBSerial.h>
    SLIPEncodedUSBSerial SLIPSerial( thisBoardsSerialUSB );
    #else
    #include <SLIPEncodedSerial.h>
     SLIPEncodedSerial SLIPSerial(Serial);
    #endif
    //&& 
    
    ////// define variables////////
    
    ////////Volatile variables needed if in interrupt//////
    volatile unsigned long timer = 0; // timer counter for pump0
    volatile unsigned long timer1 = 0; // timer counter for pump1
    volatile unsigned long timer2 = 0; // timer counter for pump2
    volatile unsigned long timer3 = 0; // timer counter for pump3 
    
    volatile unsigned long counter = 0;//counter and counter1 help in interrupt to adjust for 1us delay times while stepping a pump
    volatile unsigned long counter1 = 0;
    
    volatile unsigned long delayUS = 100000; // delay timer, could this also be 0 for the start, or a high number so that it doesn't squeak when powering up?
    volatile unsigned long delayUS1 = 100000; // delay timer
    volatile unsigned long delayUS2 = 100000; // delay timer
    volatile unsigned long delayUS3 = 100000; // delay timer
    
    ///////SLIPserial/ OSC ///////
    int32_t inDirection = 0;     // pump0 incoming OSC direction (first received integer)
    int32_t inValue = 0;         // pump0 incoming OSC flowrate (second received integer)
    
    int32_t inDirection1 = 0;     // pump1 incoming OSC direction (third received integer)
    int32_t inValue1 = 0;         // pump1 incoming OSC flowrate (fourth received integer)
    
    int32_t inDirection2 = 0;     // pump2 incoming OSC direction (fifth received integer)
    int32_t inValue2 = 0;         // pump2 incoming OSC flowrate (sixth received integer)
    
    int32_t inDirection3 = 0;     // pump3 incoming OSC direction (seventh received integer)
    int32_t inValue3 = 0;         // pump3 incoming OSC flowrate (eighth received integer)
    
    
    
    
    //////normal variables////
    int enableDrive = 1; //if enabled timer can tick
    int directionInState = 0; //direction pump0
    int directionInState1 = 0; //direction pump1
    int directionInState2 = 0; //direction pump2
    int directionInState3 = 0; //direction pump3
       
    
    //pins
    const int steppin = 3;  // pump0; the pin that is used for making the nema-motor step
    const int directionpin = 2; // pump0; the pin that lets the stepper board know which direction to step
    
    const int steppin1 = 6;  // pump1
    const int directionpin1 = 5; // pump1
    
    const int steppin2 = 9;  // pump2
    const int directionpin2 = 8; // pump2
    
    const int steppin3 = 12;  // pump3
    const int directionpin3 = 11; // pump3
    
    void setup(void)
    {
      ///// setup the pins to input or output
      
      pinMode(directionpin, OUTPUT); // pump0; direction out to drive board
      pinMode(steppin, OUTPUT); // pump0; pin that does the stepping
      
      pinMode(directionpin1, OUTPUT); // pump1; 
      pinMode(steppin1, OUTPUT); // pump1; 
      
      pinMode(directionpin2, OUTPUT); // pump2; 
      pinMode(steppin2, OUTPUT); // pump2; 
      
      pinMode(directionpin3, OUTPUT); // pump3; 
      pinMode(steppin3, OUTPUT); // pump3; 
      
      //initialize timer
      Timer1.initialize(10);//interrupt will occur every 10 microseconds
      Timer1.attachInterrupt(clickmove); // clickmove will run every 10 microseconds

      //&&
      // initialize SLIPserial communications:
      //begin SLIPSerial just like Serial
      SLIPSerial.begin(115200);   // set this as high as you can reliably run on your platform
      #if ARDUINO >= 100
          while(!Serial)
            ;   // Leonardo bug
      #endif 
      //&&
    }
    
    /////////////////////////////////////////
    /////this is the interrupt///////////////
    ////which runs every 10 microseconds/////
    /////////////////////////////////////////
    
    void clickmove(void)
    {
      
      //pump0
       if(timer+counter1 >= delayUS) ///counter1 has the number of stepping occurances from last cycle (every step 'costs' one us)
          {
          if(enableDrive==1)
            {
              digitalWrite(steppin, 1); //step-pin on
            } //could use digitalWriteFast library here
          delayMicroseconds(1);
          digitalWrite(steppin, 0); //step-pin off, should I use digitalwritefast here?
          timer=0; //sets time for this pump to 0 when stepped
          counter=counter+1; ///if steppin is triggered it waits for 1us
         }
         timer=timer+10; //this counts timer up in '10usecond steps' every time the interrupt runs and compares delayUS with it
        
      //pump1
       if(timer1+counter1 >= delayUS1) 
          {
          if(enableDrive==1)
            {
              digitalWrite(steppin1, 1); //step-pin on
            } 
          delayMicroseconds(1);
          digitalWrite(steppin1, 0); //step-pin off
          timer1=0;  
          counter=counter+1;    
         }
         timer1=timer1+10;
     
      //pump2
       if(timer2+counter1 >= delayUS2) 
          {
          if(enableDrive==1)
            {
              digitalWrite(steppin2, 1); //step-pin on
            } 
          delayMicroseconds(1);
          digitalWrite(steppin2, 0); //step-pin off
          timer2=0;   
          counter=counter+1;     
         }
         timer2=timer2+10;
         
      //pump3
       if(timer3+counter1 >= delayUS3) 
          {
          if(enableDrive==1)
            {
              digitalWrite(steppin3, 1); //step-pin on
            } //could use digitalWriteFast library here
          delayMicroseconds(1);
          digitalWrite(steppin3, 0); //step-pin off
          timer3=0; 
          counter=counter+1;       
         }
        timer3=timer3+10;
        counter1 = 0; //reset counter1
        counter1 = counter; //make counter1 to counter to be able to adjust timing
        counter = 0; //reset counter after every time interrupt runs
    }
    
    
    /////////////////////////////////
    ///////main loop cycle///////////
    /////////////////////////////////
    void loop(void)
    {
        //////////////////////////////////////////////////////////////////////////
        // transfer OSC values with SLIPserial to and from PD and work with it ///
        //////////////////////////////////////////////////////////////////////////

          //&&
          //OSC slipserial incoming communication
           OSCMessage messageIN(""); //left empty because the code doesn't seem to discriminate on it
             int size;
             while(!SLIPSerial.endofPacket())
             if ((size =SLIPSerial.available()) > 0)
               {
                  while(size--)
                  messageIN.fill(SLIPSerial.read());
               }
               
               if(!messageIN.hasError())
                 {
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

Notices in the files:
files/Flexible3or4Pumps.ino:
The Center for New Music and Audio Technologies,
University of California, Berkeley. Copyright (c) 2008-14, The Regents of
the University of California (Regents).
